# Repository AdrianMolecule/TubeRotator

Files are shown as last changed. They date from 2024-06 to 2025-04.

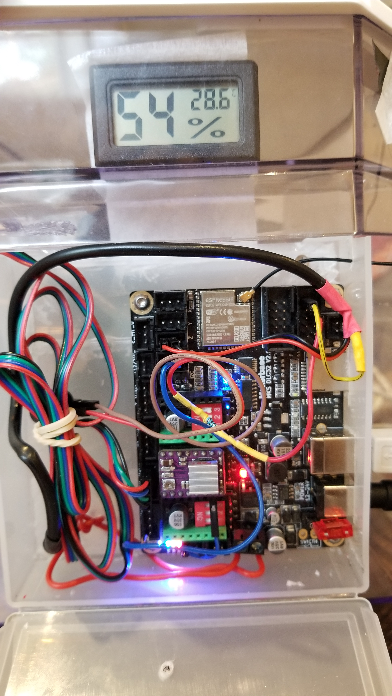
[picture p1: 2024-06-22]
pictures/mksboardConnexions.jpg

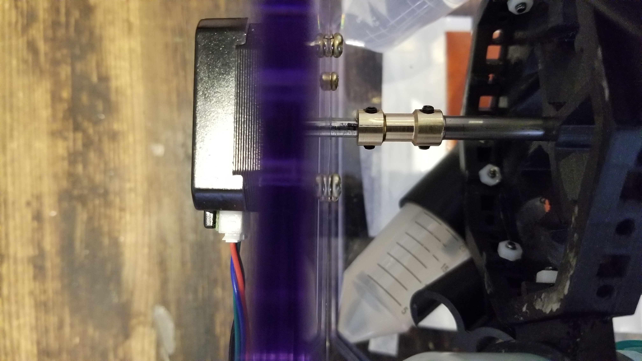
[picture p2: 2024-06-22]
pictures/rot1.jpg

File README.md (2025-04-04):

# tubeRotator
A classic tube rotator to be used for what you desire to. In a pinch it could be used as a mini bioreactor.
Software is https://github.com/AdrianMolecule/OrbitalShakerMksBoard. Sorry for 2 repos but it seems to be the only way to do it decently in gitHub.
Normally can rotate 8 50 ml tubes and about 16 2 ml or 1.5 ml tubes in the same time from 0 to maybe 300 RPM before things start flying.

It takes a Nema 17 stepper but can be chaged for a more powerful (why I don't know) stepper which requires changing the hole positions in the rotor mount file.
By default the rotation is  80 RPM but it could be change to any value by using a serial terminal commands.
If you are interested I can also add a Wifi interface for changing speed and temperature.
It's tested and true.
Don't forget to leave tubes mostly empty if you want to grow e-coli. I normally use 1 to 2 ml LB media in a 10 ml tube. Don't forget that even then, the oxygen will almost ran out after about 7 hours.

Assembly Steps
Check your MKS board and the motor -Put in one stepper driver in the middle slot, connect power and serial port and then try the motor with the board separately first using the preinstalled MKS software and a CNC Laser cutter program like LaserGRBL. Check movement on Y axis.
Wire the board using the jumper cables, load our software on the board and try it after. If you want to do the driver current optimization described later after *.
Print parts without support in ABS if you can but I think PLA will work too. The template is just for marking where to drill the motor mounting holes but you can use the balljoint holder for that if you want.
Connect the desired holders with the rotor with screws or snap them with magnets
Assemble the rotating mechanical parts inside your box, try again
Print or get a board box, put the board supports, close the box and retry
Attach the board box to the main box.

BOM:
MKS DLC V?? with the cable for the serial port that normally comes with and at least one stepper driver ic that normally comes with. Better get the low noise one for obvious reasons.
6 mm rod. Mine came from either an old printer or a empty laser printer tonner cartridge.
6 mm internal diameter ball joint - Optional in case you want to support the shaft at both ends. I don't do that anymore!
6 mm to 5 mm shaft coupler. You can use a rigid one or the helice spring aluminium one. I tried both, the spring one is smoother at start depending on speed but I settled for the cheap fixed one. For example https://www.aliexpress.com/item/4000221326289.html?spm=a2g0o.order_list.order_list_main.5.2e7b18023d0EkV or https://www.aliexpress.com/item/4000589186252.html?spm=a2g0o.order_list.order_list_main.10.2e7b18023d0EkV
For holding the tubes you need either 8x 3 mm screws of about 15 mm or longer or 32 magnets of 12x6x2 mm.
More screws and nuts- all 3 mm 
4 x3mm screws for attaching the motor and at least 2 more for attaching the balljoint part. You need to determine the length based on how thinck you box is. 
Also at least 3 for attaching the MKS board box to your box and 4 more special screws to attach the MKS board to its box like https://www.aliexpress.com/item/33054086915.html?spm=a2g0o.order_list.order_list_main.151.2e7b18023d0EkV
Any Nema 17 stepper including flatter pancake ones like https://www.aliexpress.com/item/1005007016114666.html?spm=a2g0o.productlist.main.35.7f774895AlZWFk&algo_pvid=77c29ec8-36eb-487f-abc6-7f73ea85a693&algo_exp_id=77c29ec8-36eb-487f-abc6-7f73ea85a693-12&pdp_npi=4%40dis%21CAD%2113.28%2113.28%21%21%219.45%219.45%21%402103011017184219655302441e2644%2112000039081821468%21sea%21CA%21132308507%21&curPageLogUid=Vj7nNkeNSwOw&utparam-url=scene%3Asearch%7Cquery_from%3A
Options: you can use a bigger or smaller rod as long as the internal diam or the ball joint and one end of the shaft coupler mathes that bigger or samller diameter. So for instance 4 mm or 10 mm. You will also have to change the shaftDiam param inside the Fusion360 file and regenerate only the tube rotator (wheel) 3D printed file.
Some kind of enclosure about 250x190x-170mm, ideally with a door and partially transparent. Mine was an acrylic box from a water filter.
About 10 or less female to female pin connectors -2.54mm Dupont Line 20cm 10cm 40Pin  Female to Female like  https://www.aliexpress.com/item/32481623557.html?spm=a2g0o.order_list.order_list_main.69.e1ec1802BAvD1N
An old laptop adapter (mine is 18.5V) that matches the jack of the MKS board or you can either buy a jack adapter (you need to search for that so it matches your adapter and the MKS board) or you need to splice in a new jack after removing the original adapter jack. Could be anywhere from 12 V to about 25 V.
You can use the
Another short 3 mm screw in case the shaft hole does not hold the rod. Alternatively you can also use glue or just jam it with some tape on the rod
If you use magnets and they trend to come off their sockets you can also use glue.
I usually print in ABS whith no support and sometimes I use brims for holders in case it does not stick to the bed.
That is all for the rotator only part.

If you want the heater incubator part too:
You need need the power board a temperature sensor and a silicone heating pad of 12 or 24 volts. You will need to futher insulate the box in case you'll find that it takes too long to reach the desired temperature- usually 37 Celsius. You power the heat pad directly from the spindle (2 screws). I limited the max power to about 90%. It's important to put some metal holder under the heater otherwise it might melt the box. I used some tin leftovers fro some fascia cover but you can use a tin can. Careful when cutting it- use thick gloves.

No soldering should be required but 2 resistors need to be connected somehow, one is series with the piezo buzzer and one between + and signal pin on the temperature sensor. Their leads can be just spiralled around their connexion and electrical tape can be used for isolation. I did solder them and used shrink wrap for insulation but it's not necessary. As a matter of facts the buzzer itself could be considered optional.

**If you want to optimize the torque for the Nema motor, Google it on youTube. When using a noisier driver like DRV8825  watch=> https://www.youtube.com/watch?v=Vp9ZRCEhVYc . That could be different if you get the quiet driver so add the name of your driver to the Google search. I used the DRV8825 without noise issues.

At this point you can set the target RPM and target temperature using the serial port. Use CoolTerm (Free program) to connect to the serial port and type ? to see possible commands. At this point you can start stop the rotation, set the rotation speed and set the temperature. 
Sometimes on higher load depending on what motor you are using it migh not start until you give it a push with your finger. That is not necessary for me if I fully load the wheel with 50% filled tubes. Normally you will not fill the tubes more than 20% to have enough Oxygen but for other tasks that might not happen.

One simple way to accommodate smaller tubes is to put them in the 50 mm tubes with something to block them for moving (I use pieces of sponges)

Normally you get a faster delivery, better support on Amazon. All the links are just example and I encourage you to find beter one with better reviews, delivery, quality etc.
I built this as a quiter alternative to the orbital shaker. That's for making many glycerol stocks at the same time but it could be used for incubation or even as mini-bioreactor.

As with all projects, we looked at many existing devices and while we did not really copy anything from any of them there are natural similarities given the task. 

Special thank to Sebastian Cocioba who had published a similar device in OS. His designs are always true and his work is fantastic.
Update: the .stl files and the previous fusion360 show the model in the pictures that has been in use for a year or longer.

I just uploaded a new much slimmer model that also supports both screws or 5 mm cube magnets. As for the previous model you need at least 16 but better use 32 that gives you 8 large holders. The .stls are in the slimStls folder. This new model does not add new functionality but it's just much shorter to print.

I discovered that a short shaft that is only supported on the motor side is enough for rotation as long as the rotor is pushed closed to the motor. Sou don't need to print the orther end shaft support.

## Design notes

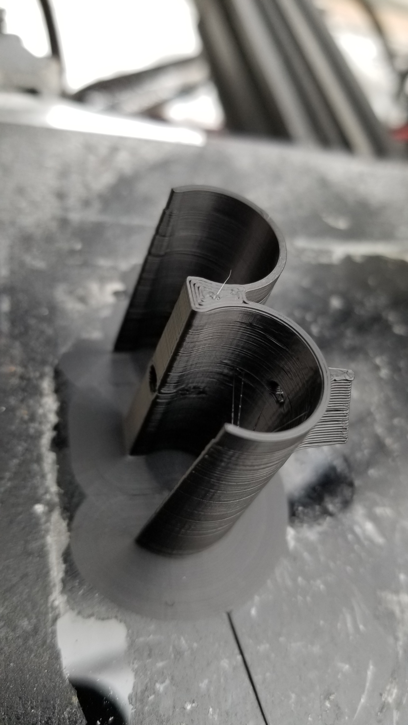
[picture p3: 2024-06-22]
pictures/small10mlholder.jpg

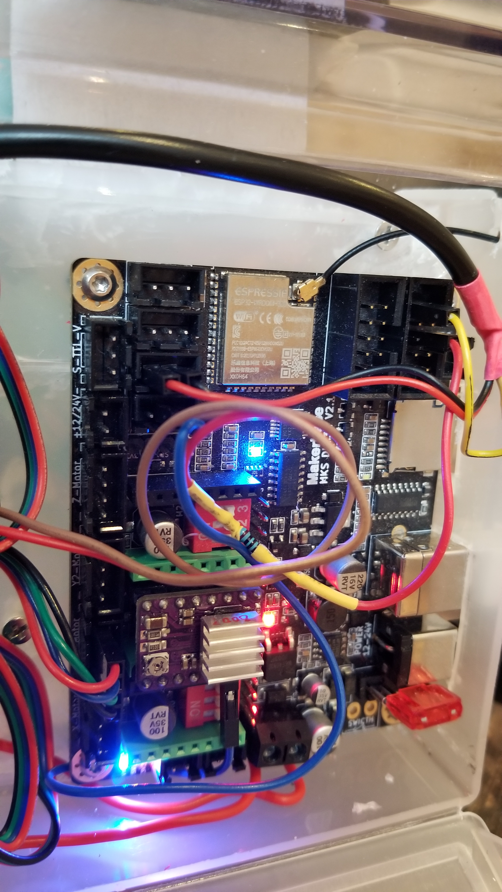
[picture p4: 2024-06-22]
pictures/mksboardConnexions1.jpg

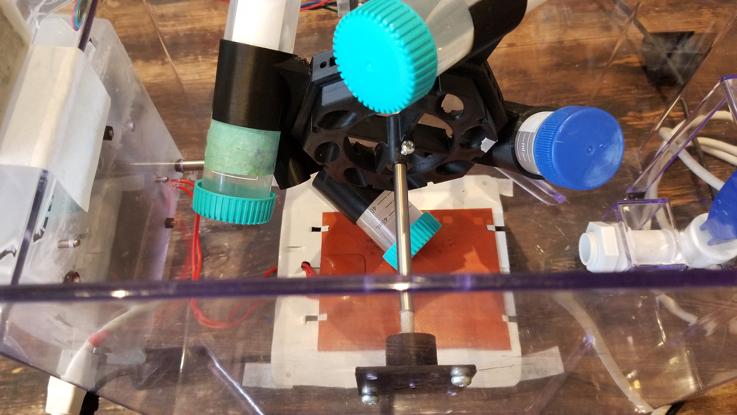
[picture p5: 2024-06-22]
pictures/rot6.jpg

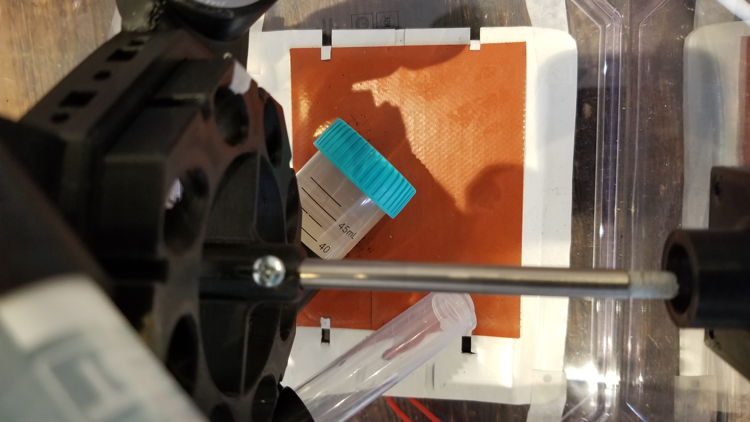
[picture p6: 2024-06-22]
pictures/rot8.jpg

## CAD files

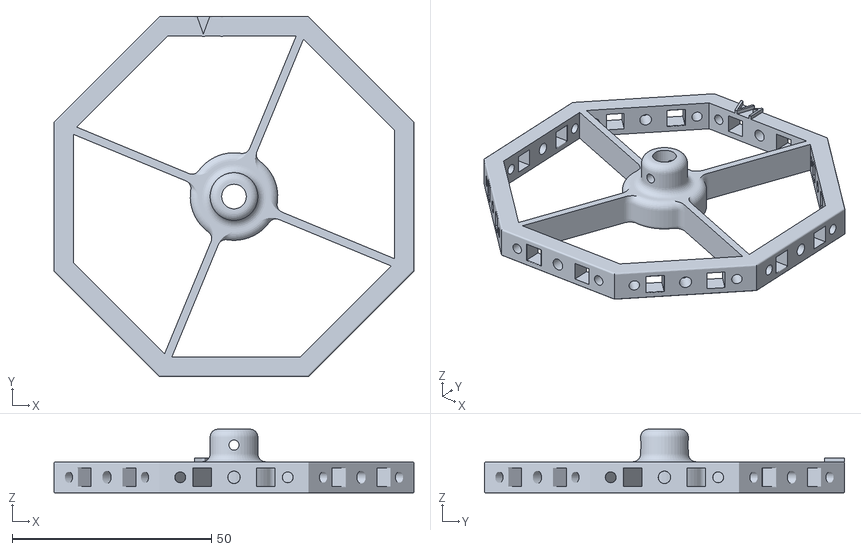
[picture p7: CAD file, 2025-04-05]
slimStls/tube rotator 5 mm magnet Min v7.stl
90.4 x 90.4 x 16.0

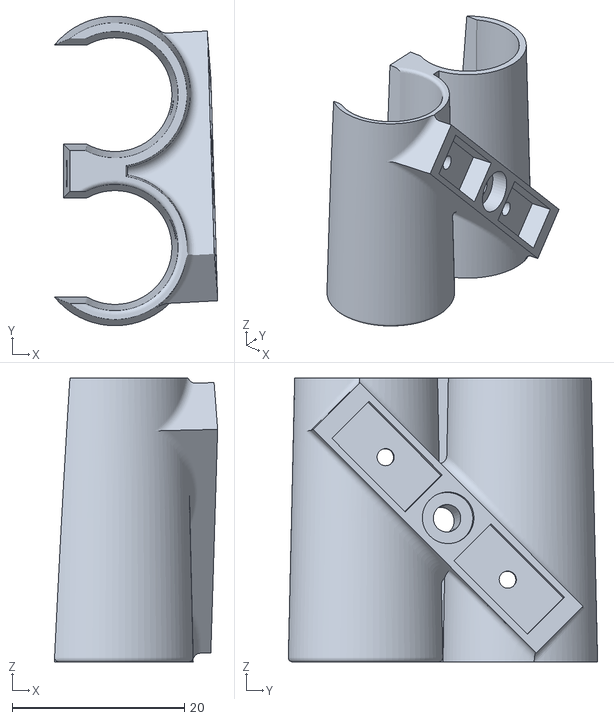
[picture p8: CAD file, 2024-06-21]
stls/tubeHolder2307.stl
19.0 x 35.9 x 33.0

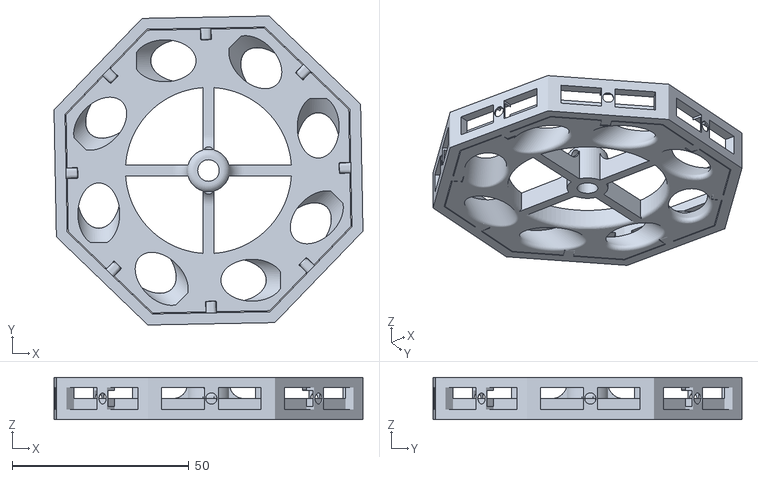
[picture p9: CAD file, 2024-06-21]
stls/tube rotator 12by6by3 v8.stl
87.5 x 87.5 x 12.0

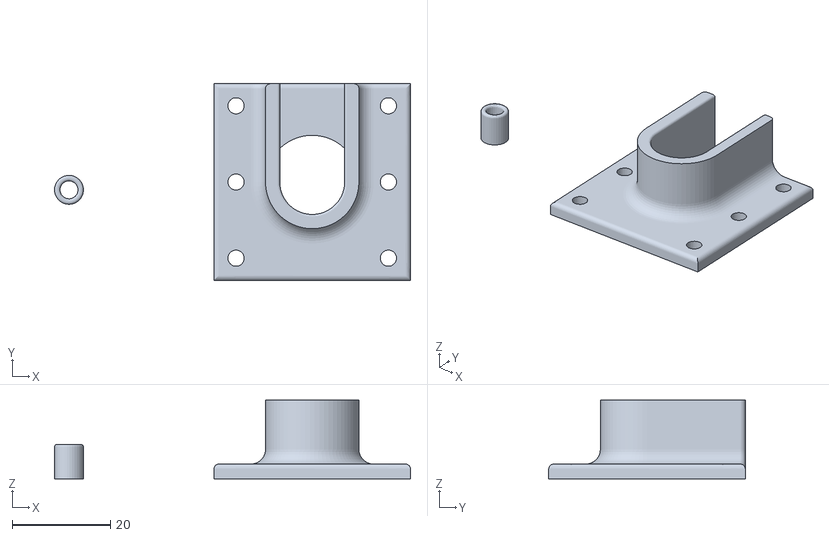
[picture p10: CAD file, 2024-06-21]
stls/bearingHolder.stl
72.4 x 40.0 x 16.0

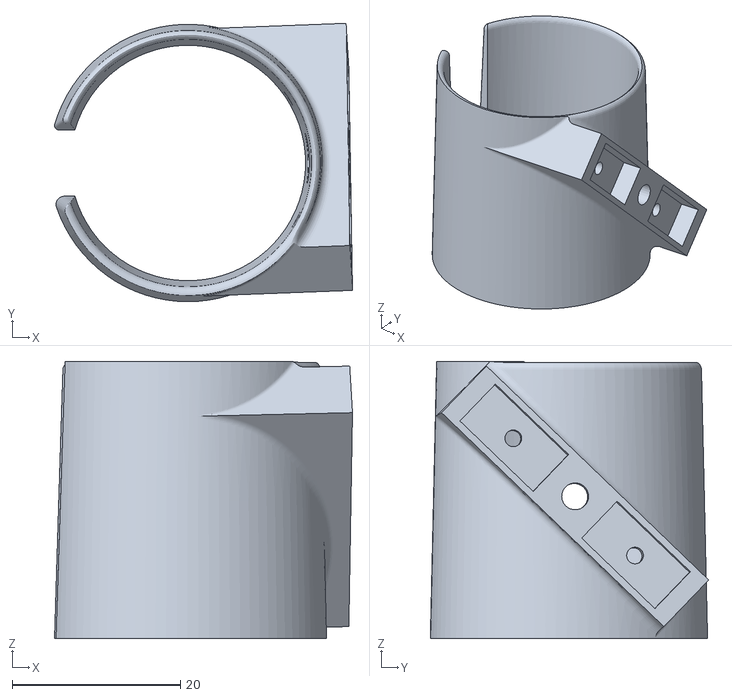
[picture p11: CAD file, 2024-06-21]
stls/largeHolder.stl
35.5 x 33.1 x 33.0

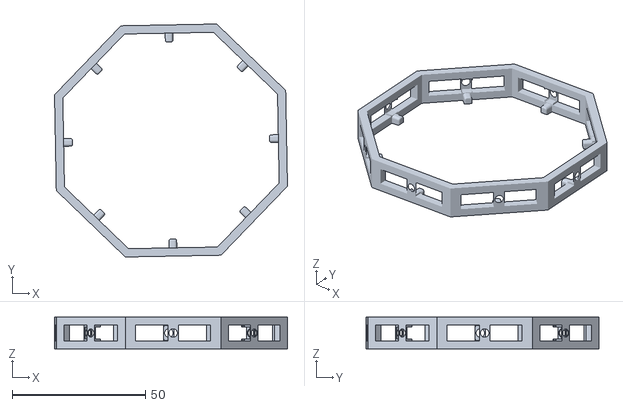
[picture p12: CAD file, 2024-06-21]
stls/ring.stl
87.5 x 87.5 x 12.0

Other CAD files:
stls/10mlTubeHolder.stl
tube rotator 12by6by3 v12.f3d
tube rotator 5 mm magnet Min v7.f3d

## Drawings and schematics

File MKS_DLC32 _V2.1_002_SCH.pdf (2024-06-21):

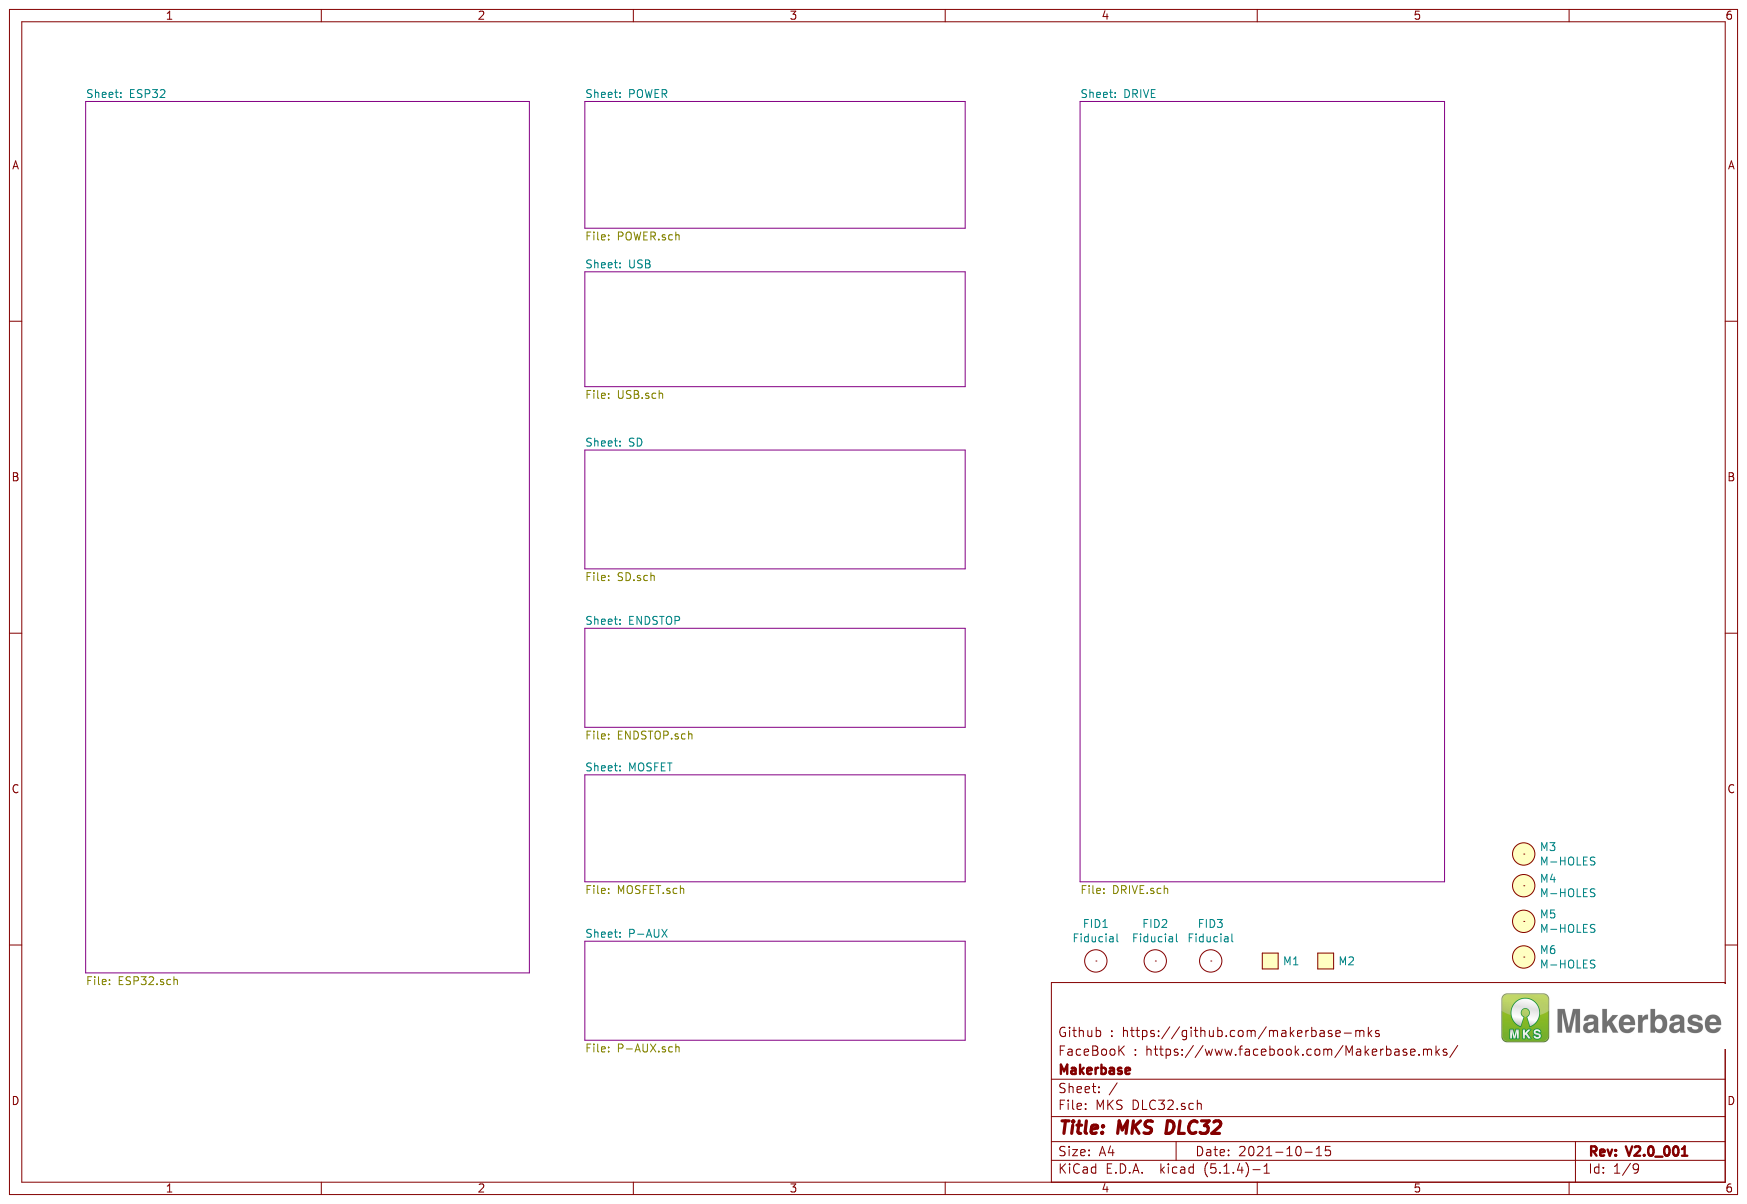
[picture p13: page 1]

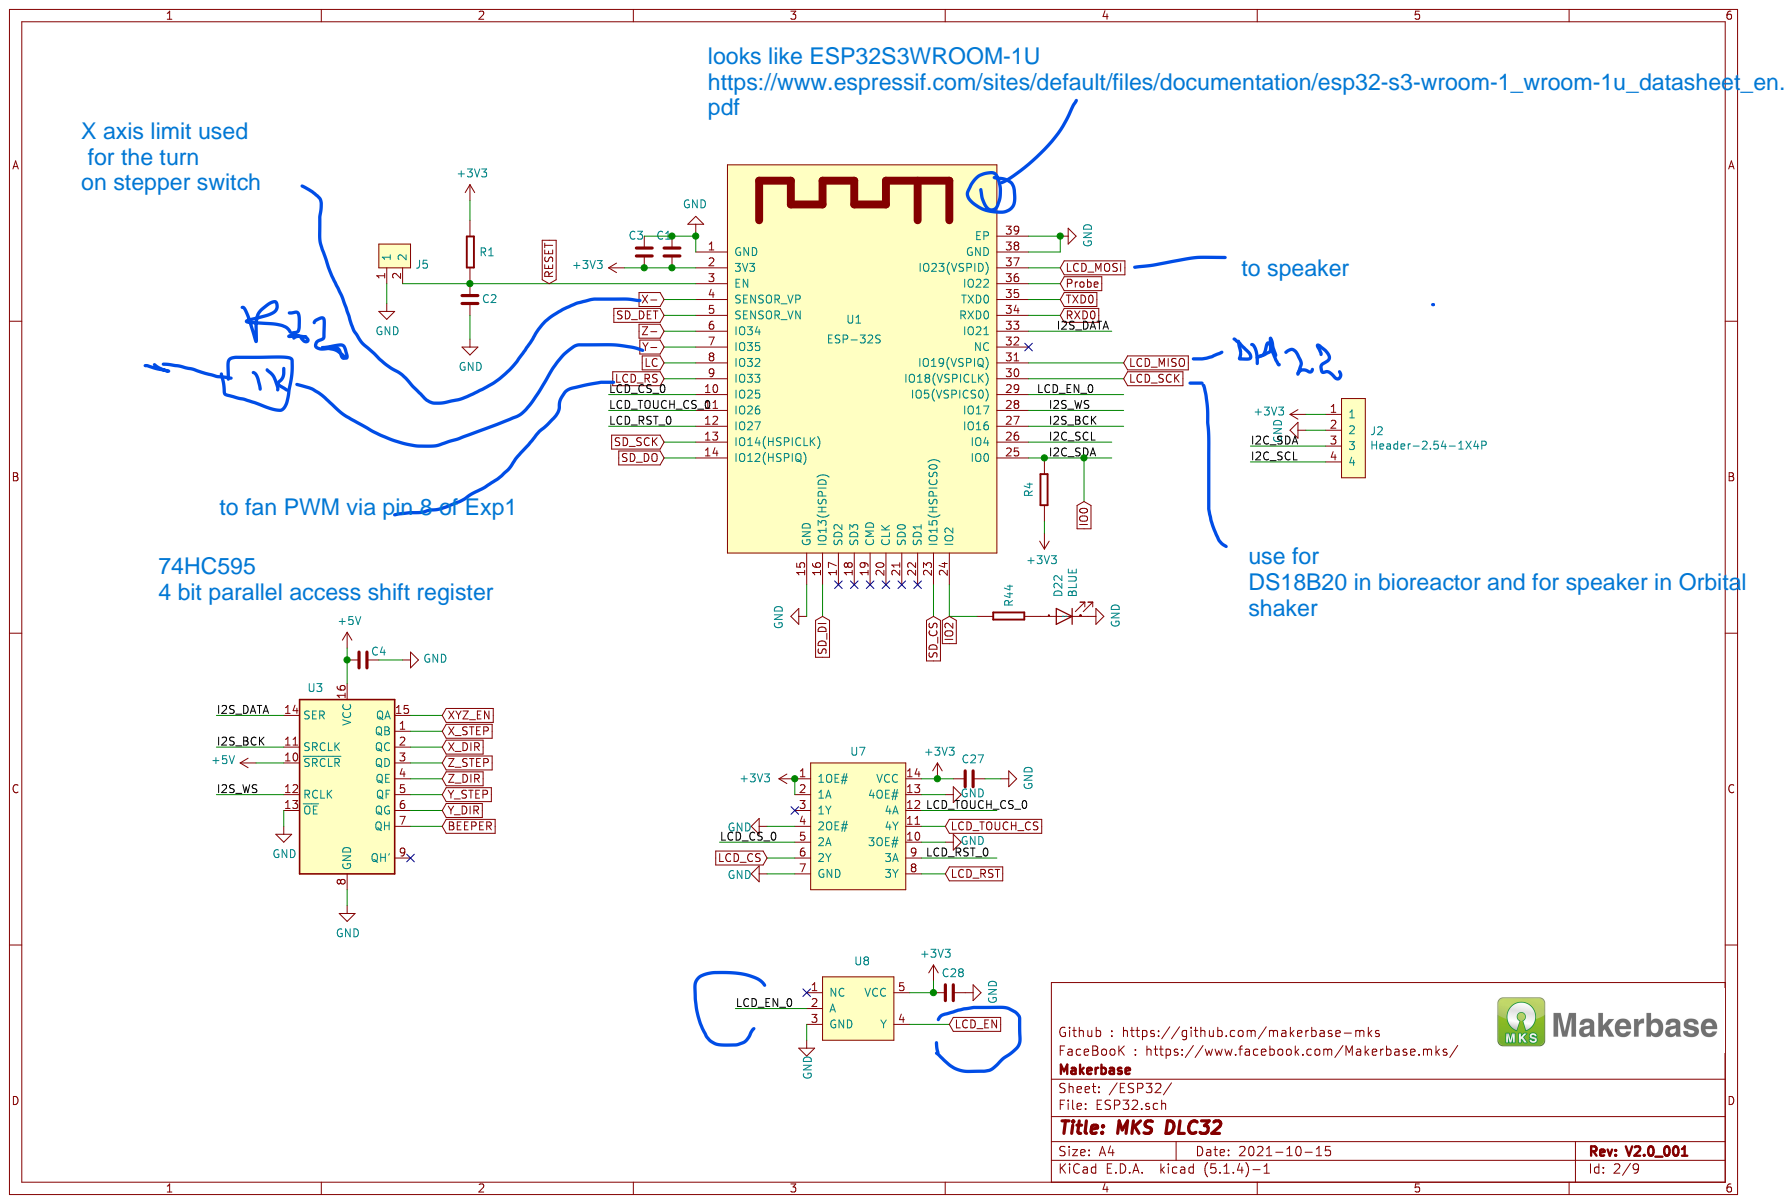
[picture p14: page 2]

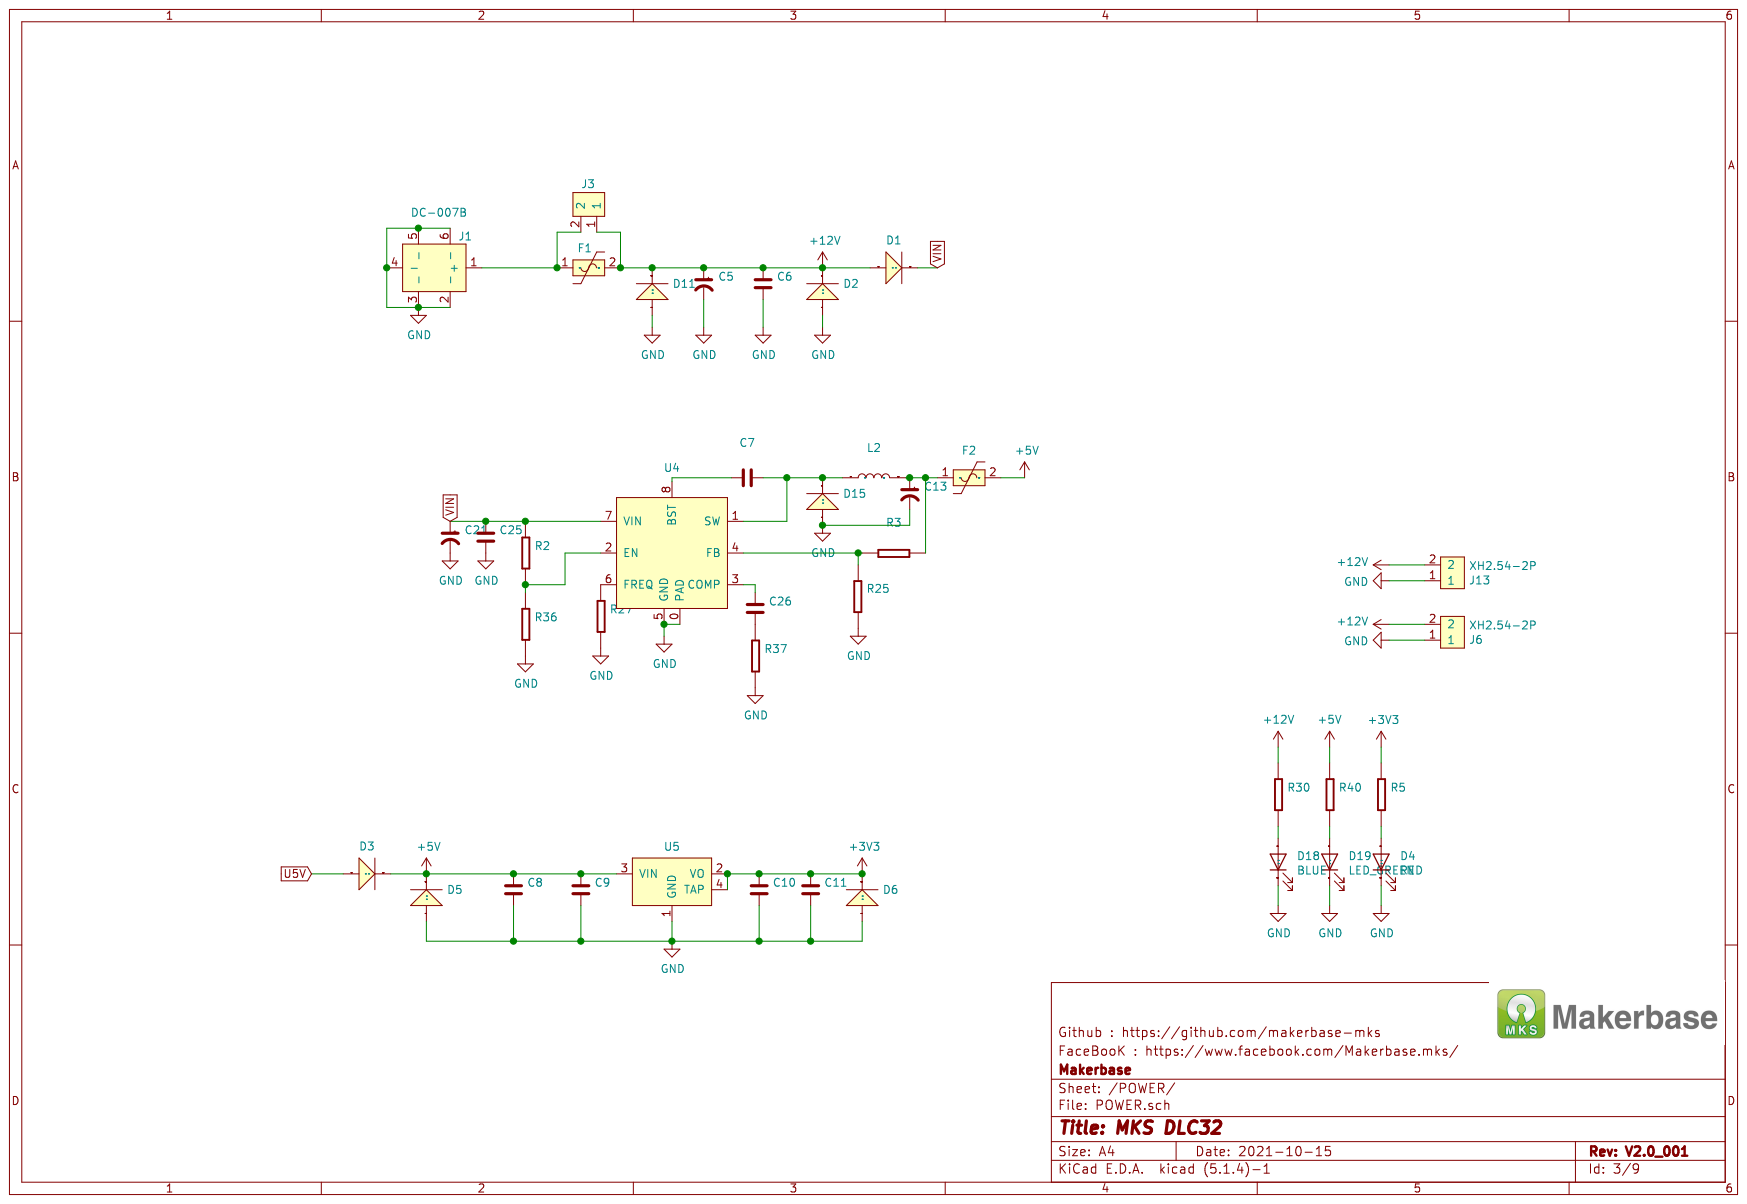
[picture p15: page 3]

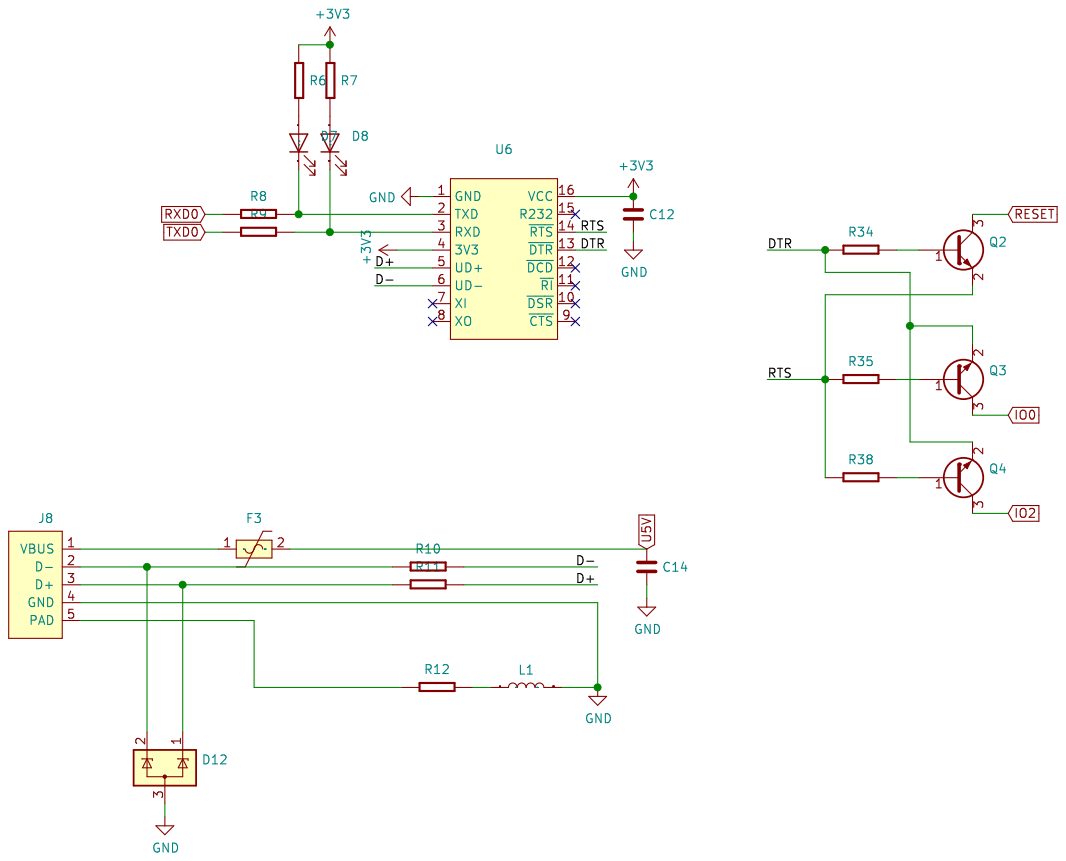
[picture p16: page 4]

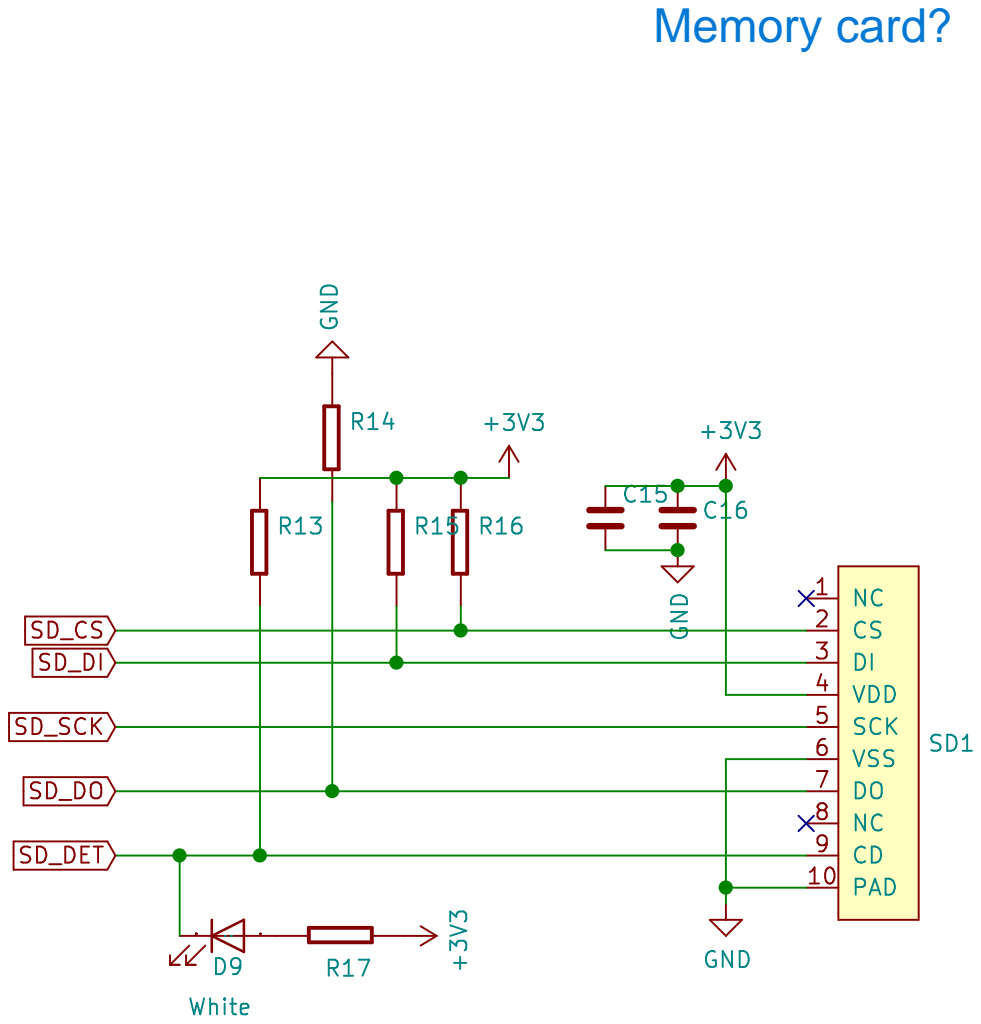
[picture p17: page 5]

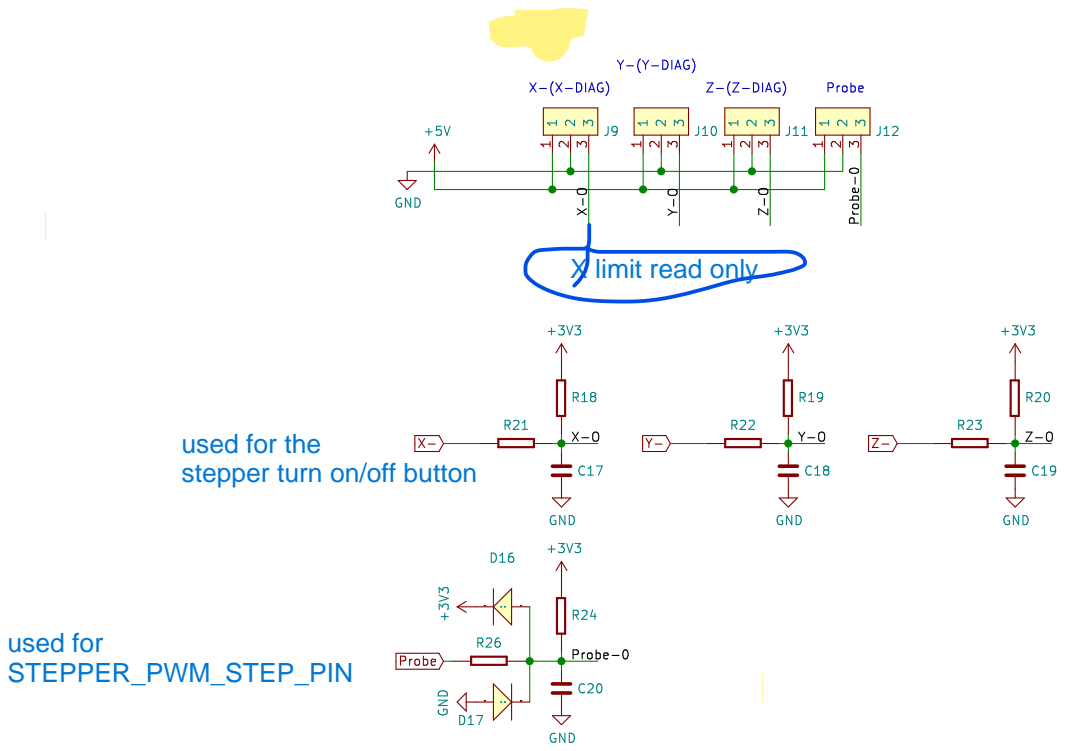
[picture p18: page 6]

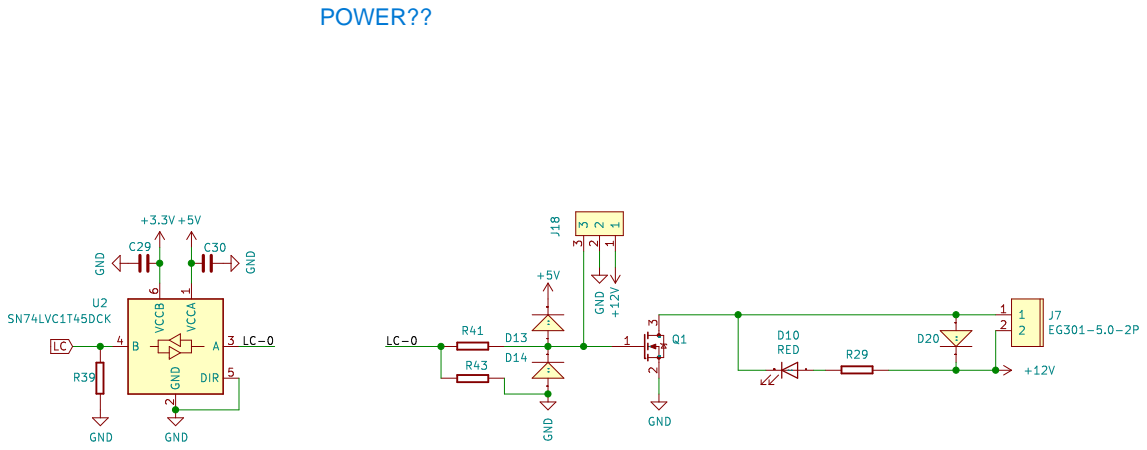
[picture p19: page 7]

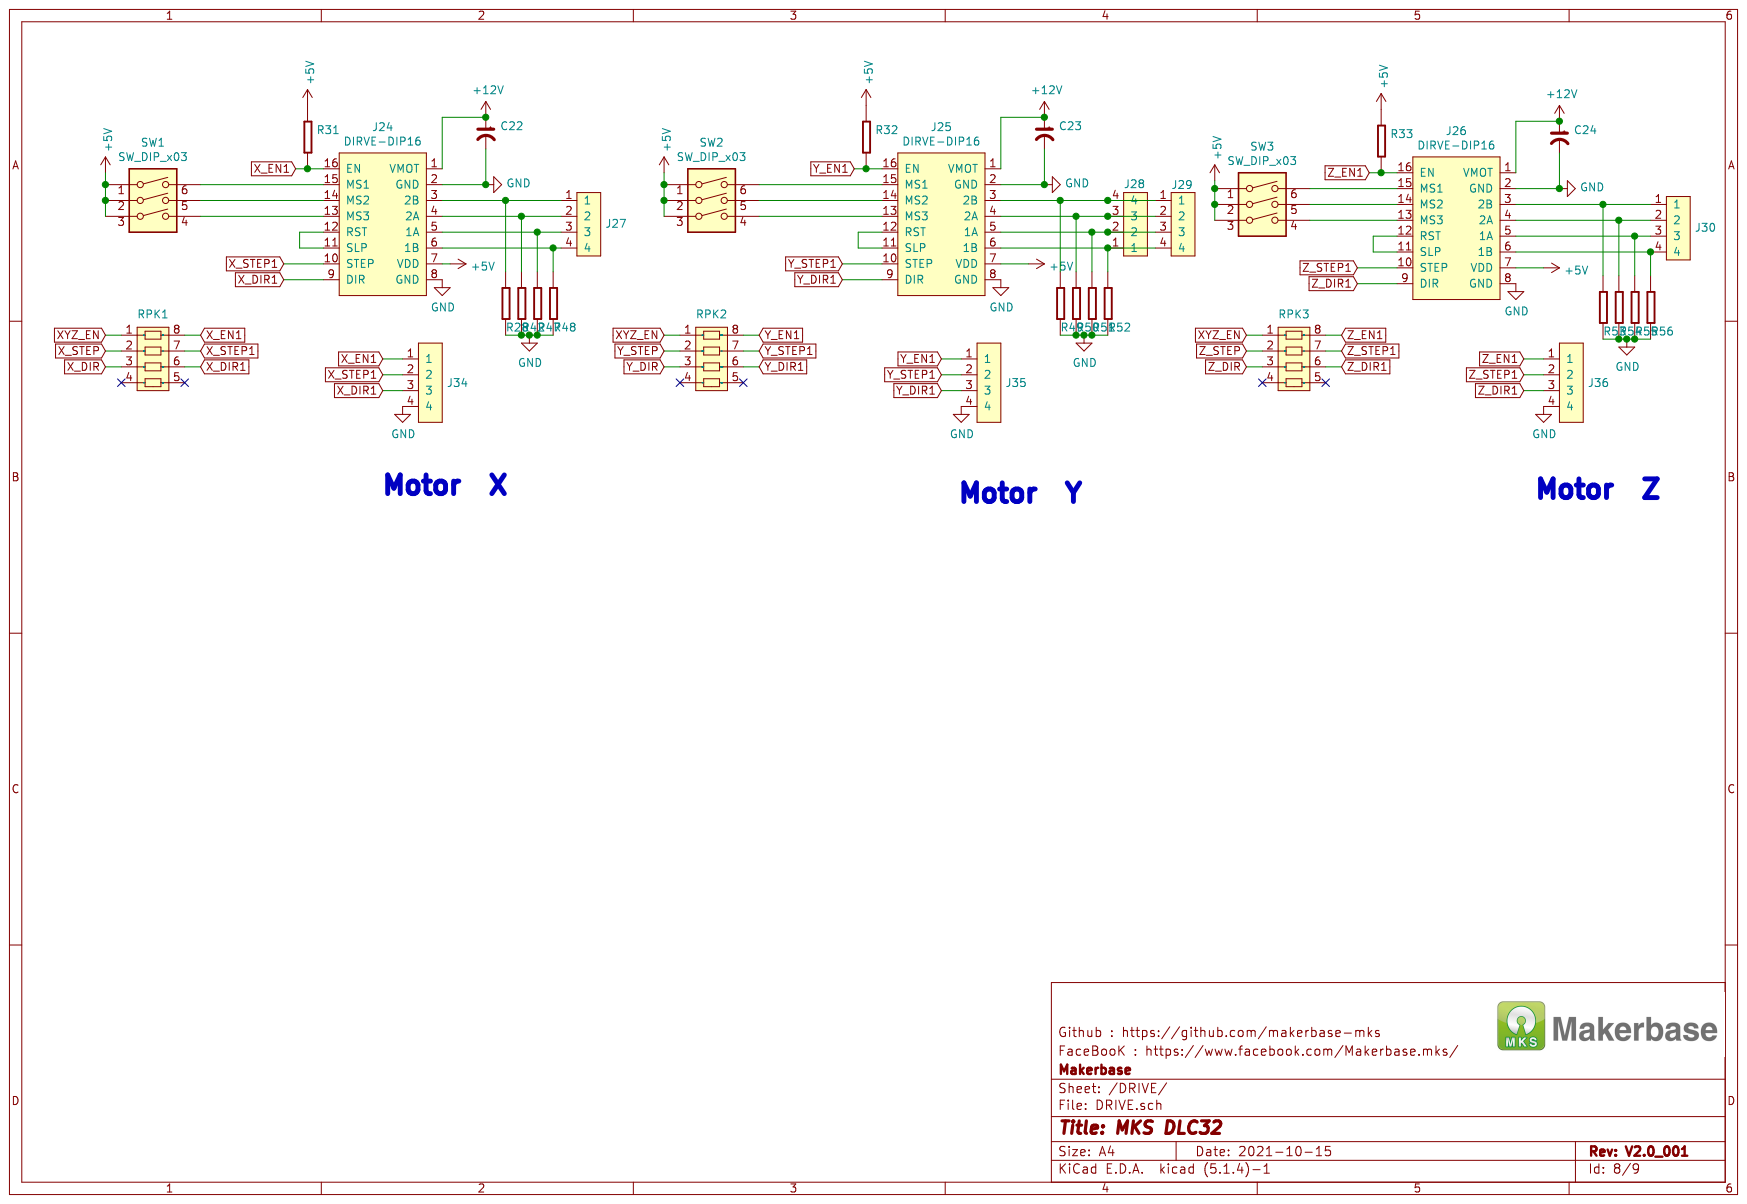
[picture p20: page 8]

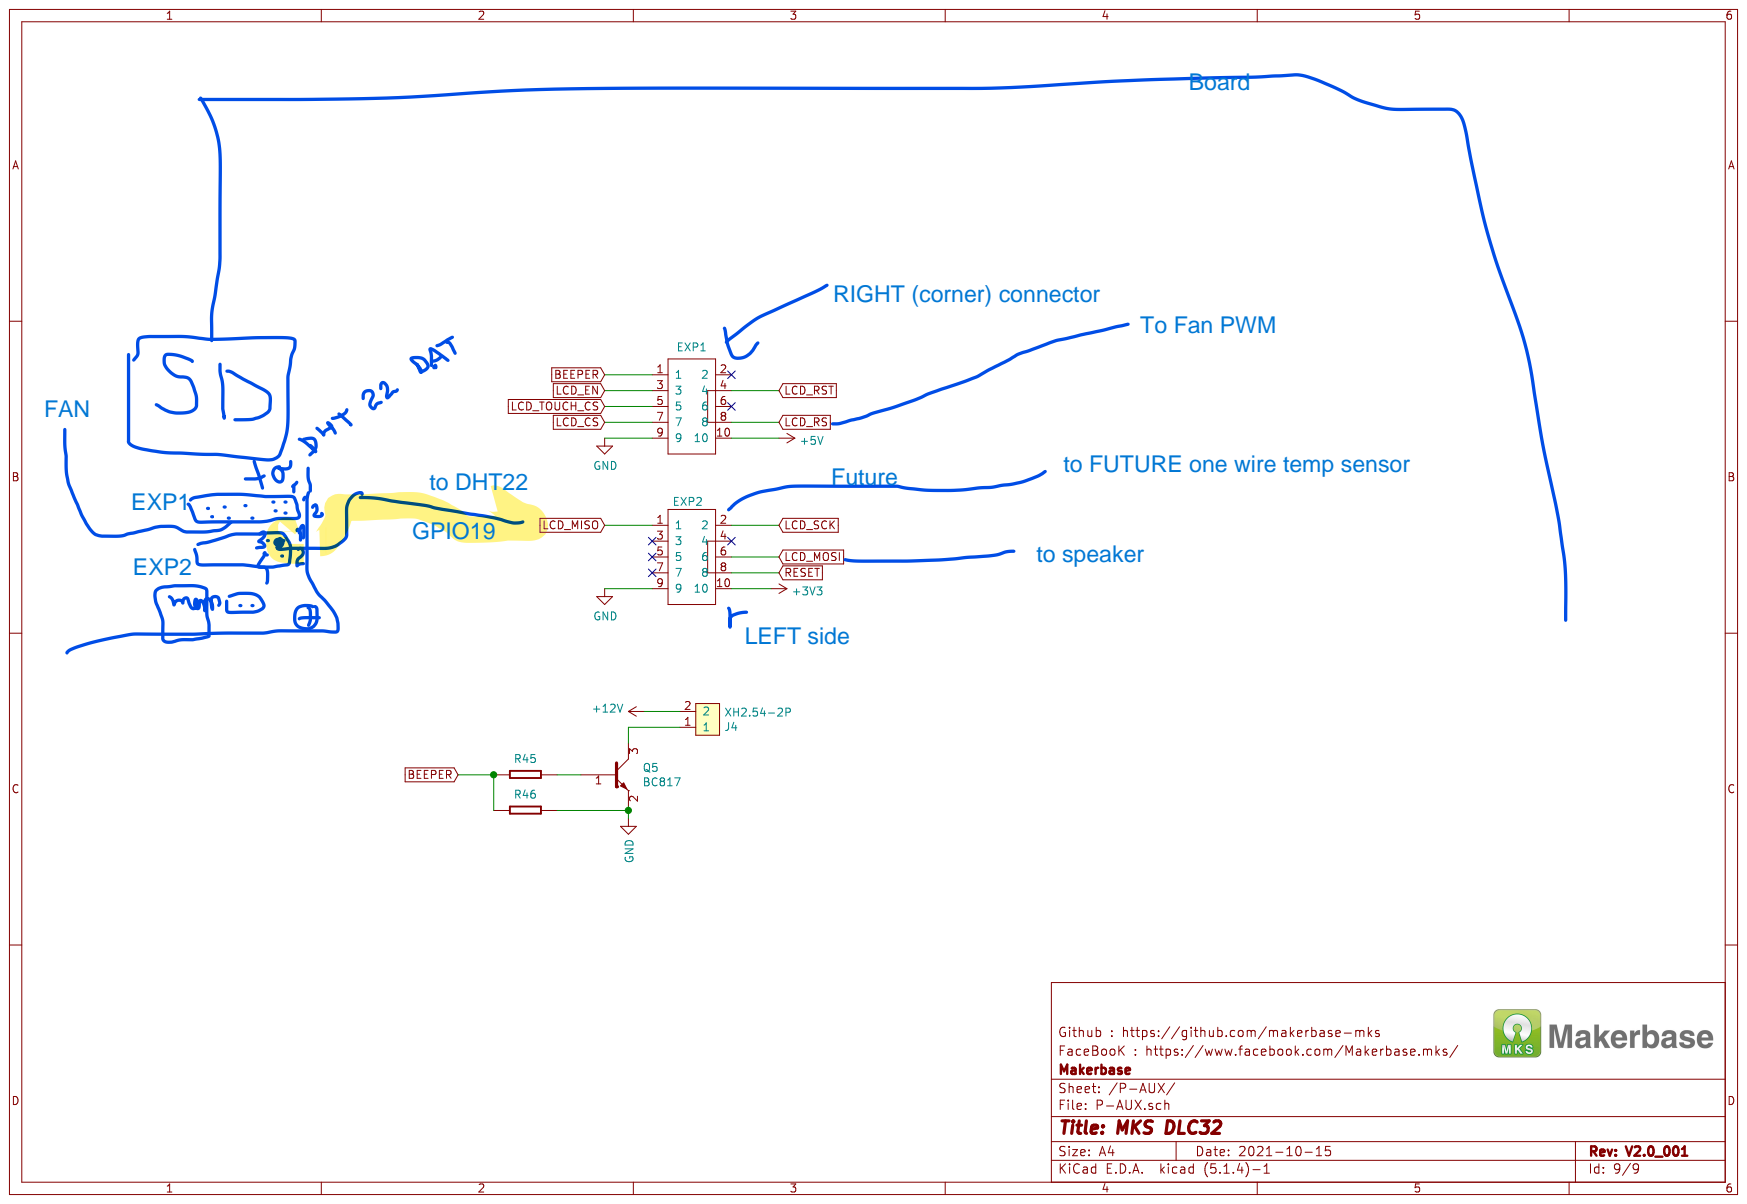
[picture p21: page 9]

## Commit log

2024-06-21 Add existing files
    [10mlTubeHolder.stl, bearingHolder.stl, largeHolder.stl, ring.stl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]
2025-04-04 A new much slimmer model that takes less to print
    Supports both screws or 5 mm cube magnets. need at least 16 but better use 32 that gives you 8 large holders
    [tube rotator 5 mm magnet Min v5.f3d]
2025-04-04 slim stls
    [wheel tube rotator 5 mm magnet Min v5.stl]
